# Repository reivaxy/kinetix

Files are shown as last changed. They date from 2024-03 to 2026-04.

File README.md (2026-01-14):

# KINETIX HAND

[French](https://github-com.translate.goog/reivaxy/kinetix?_x_tr_sl=en&_x_tr_tl=fr&_x_tr_hl=fr)
[Spanish](https://github-com.translate.goog/reivaxy/kinetix?_x_tr_sl=en&_x_tr_tl=es&_x_tr_hl=fr)
[German](https://github-com.translate.goog/reivaxy/kinetix?_x_tr_sl=en&_x_tr_tl=de&_x_tr_hl=fr)
[English](https://github.com/reivaxy/kinetix)

The cost is estimated less than $40, depending on where your order parts from, and the weight is less than 300g.

BOM: https://github.com/reivaxy/kinetix/blob/main/hardware/Schematics/BOM.md

Connect to your nearby KinetiX through Bluetooth here: https://reivaxy.github.io/kinetix/

> [!TIP]
> Detailed assembly instructions are available in the [wiki section](https://github.com/reivaxy/kinetix/wiki)<br/>
> 
> We suggest you read it before starting building this project to make sure you have the required tools. It is not very
> difficult, but when you don't have a soldering iron, you don't have a soldering iron 😉
> 
> **Be sure to read the "parts" chapter about the servo motors** that come in many flavors, only one of which is supported for now.

> [!TIP]
> You need not build the firmware or the android app, binaries are available in the [releases section](https://github.com/reivaxy/kinetix/releases)
> 
> **BEWARE**: for now, voice control via bluetooth is only available with the **ANDROID application**, but soon via a webpage opened in Chrome browser for all platforms where Chrome is supported.
> There is a prototype iPhone application that allows control by pressing buttons on the screen.

> [!CAUTION] 
> The work in this repository is released under licence Creative Commons 
> Attribution-NonCommercial-ShareAlike 4.0 International (CC BY-NC-SA 4.0) open-source license<br/>
> Please read this license to understand what you may and may not do with these files (software and 
> hardware):<br/> 
> https://creativecommons.org/licenses/by-nc-sa/4.0/<br/><br/>
> The 3D part of this work is based on the Kinetic Hand, created and released by Mat Bowtell:<br/>
> https://www.thingiverse.com/thing:4618922<br/><br/>
> To me, the most important part of it is "non commercial": do not use this work to sell anything, 
> in any way, no matter how derivative it is.<br/><br/>
> =============== DISCLAIMER of liability =============== <br/>
> This is not a medical device. You must not use it as a missing limb replacement without checking with
> medical professionals if this is appropriate.<br/>
> Also, this is still a work in progress and should not be used until it has reached some level of 
> completion and testing.<br/>  
> You build it and use it at your own risks.  
> 
> Contributions are welcome, please try as much as possible to respect the [contribution guidelines](./CONTRIBUTING.md), thanks!

Main features (WIP): 5 independantly controlled fingers, bluetooth connexion to control movements from a mobile phone, edit settings, wirelessly update the firmware (using also Wifi), extensibility to add sensors and more.

I've been a maker and board member of [the French e-Nable association](https://e-nable.fr/fr/) for a few years, and I've 
worked on several 3D printed devices intended for people missing part of a hand or an arm.

The most recent of these devices is the [Kinetic hand, designed by Mat Bowtell](https://www.thingiverse.com/thing:4618922), which is easy to print and assemble, with 
a smoother and more natural look than older devices such as the Phoenix Unlimbited.

These devices are muscle activated and require their user to still have a functional wrist or an elbow.
When I worked on this project, there was only one low cost motor activated 3D printed device, the [Exii Hackberry](https://www.exiii-hackberry.com/) with all the documentation needed to build it.
It's a great device, but I found it somehow uneasy to print and assemble, with many small fragile parts, it's still a bit expensive, and I thought
more recent electronic components would allow going further.

Which is why in 2023 I started to work on this project to combine both new hand design, and recent 
electronic microcontroller to drive the servomotors. I've investigated several solutions and here is the most promising one.

This is still very much a Work In Progress:
- The bluetooth connectivity is not secured, and voice control will work with anyone's voice.
- The wires tension is not adjustable
...

Like the Hackberry and unlike the Kinetic, due to tight mechanical constraints, the Kinetix can't be resized to fit smaller limbs.
I have another project (in very early stage) which might help with this, that is using only one big servo for all fingers, of course with
very different capabilities and features.

Adding a small "shield" board on top of main board, capabilities can easily be extended. This videos shows tests with a very simple pressure sensor:

https://github.com/user-attachments/assets/475526ec-1bb6-489a-a5ff-d1ec1696035d

Since May 12th 2024, it can be activated with voice control using an Android application (please enable sound on this video or it won't make much sense :) )

https://github.com/reivaxy/kinetix/assets/3592991/68d8df24-c723-40e2-a849-26ecd64f889a

And here was the early first prototype, testing speed:

https://github.com/reivaxy/kinetix/assets/3592991/b644f965-3c86-4bcd-a1fd-c3cf471b4016

Check [latest release](https://github.com/reivaxy/kinetix/releases/) for APK with voice control

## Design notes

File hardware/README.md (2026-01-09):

June 22 2024:

New version v0.4 without current monitoring but much easier to mount with a simple soldering iron (no SMDs).

This new design is modular and allows to plug an additional pcb or proto-board with specific circuitry
for instance for current monitoring or for specific sensors, etC.

Information about the board in the wiki:

https://github.com/reivaxy/kinetix/wiki/04.-Electronic-Board

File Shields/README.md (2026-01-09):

# Shields for the KinetiX main board

These are electronic boards that can be added on top of the main KinetiX board to extend its capabilities.

It takes advantage of the pins mounted on the main board to access the GPIOs of the ESP as well as the power line of the servos.

More information about the shields in the wiki:

https://github.com/reivaxy/kinetix/wiki/10.-Extension-Shields

Oled screen: https://github.com/reivaxy/kinetix/wiki/10b.-Oled-debugging-screen

Pressure sensor: https://github.com/reivaxy/kinetix/wiki/10a.-Pressure-sensor-activation

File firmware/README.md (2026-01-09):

# Software

Folder esp32 contains the actual software for the Seeed Studio XIAO ESP32S3

Beware, it won't work with the Seeed Studio XIAO ESP32C3 (C3 vs S3), some modifications would be required in the servomotor command.

You can find some information about installing the firmware in the wiki: 

https://github.com/reivaxy/kinetix/wiki/05.-Firmware

And some explanation about the code itself:

https://github.com/reivaxy/kinetix/wiki/05.-Firmware#the-code

Folder rp2040 contains preliminary tests with an early prototype on breadboard, and is no longer maintained.

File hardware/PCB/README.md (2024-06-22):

# PCB

There was a little bug on PCB v0.3, which is fixed in v0.4

If you already have or ordered version v0.3 let me know, it can be fixed with a little wire, and would only impact extension boards.

This PCB was created using the online schema and pcb editors from https://easyeda.com/editor

It only uses standard parts easy to solder with a soldering iron (SMD capacitor c1 is not mandatory)

The gerber zip file can be used to order PCBs. I ordered mine from https://jlcpcb.com, where I could get 5 pieces for under $5 shipping included.

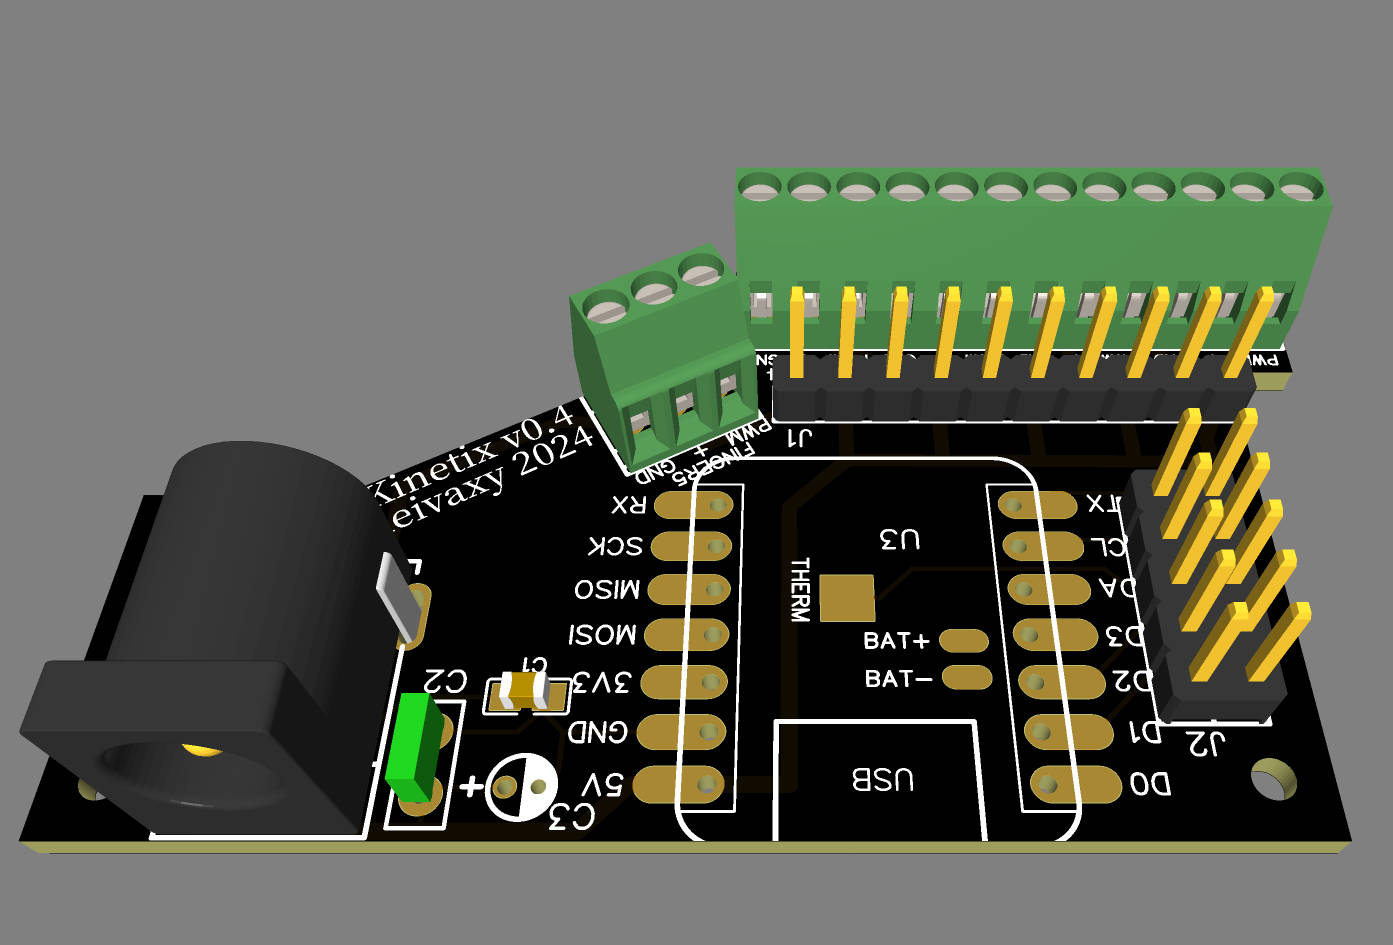
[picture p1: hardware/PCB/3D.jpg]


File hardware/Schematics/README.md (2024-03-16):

# Schematics

This schematic was created using the online schema and pcb editors from https://easyeda.com/editor

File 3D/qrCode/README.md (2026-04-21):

A small QR code stand you can use if you present a KinetiX hand at a maker fair or conference or whatever.



Should be printed in at least two colors, of course.



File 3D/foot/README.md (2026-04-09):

This is a simple foot or stand to hold your KinetiX upright.

You will need to print the "key" part twice, preferably in TPU.



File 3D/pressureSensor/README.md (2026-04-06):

# Pressure sensor case

The base is printed in PLA, the press in TPU.

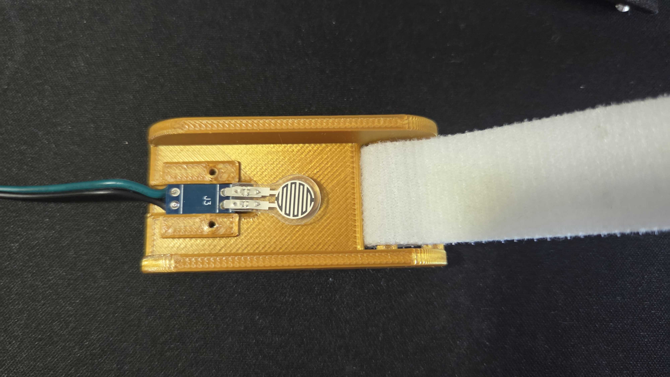
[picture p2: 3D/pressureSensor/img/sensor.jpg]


A small piece of pcb is used to hold the sensor in place, and it's then cover with a TPU piece ensuring a soft press on the sensor.

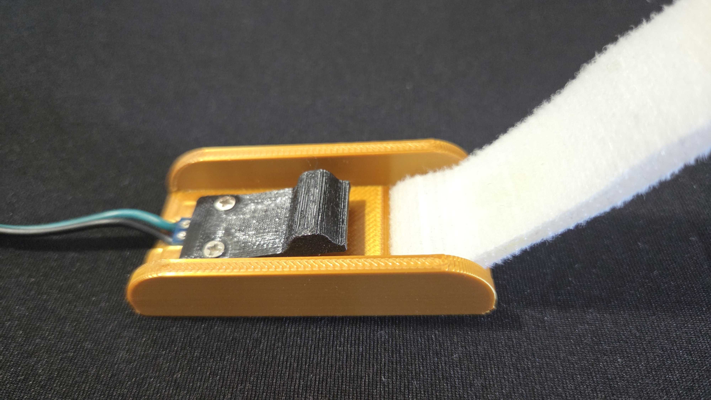
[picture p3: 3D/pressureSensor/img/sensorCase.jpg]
 

The arm band must first cover the sensor (to the left on the picture), then go around the arm, then up trough the case slot, then back around the arm and scratch to the part above the case.

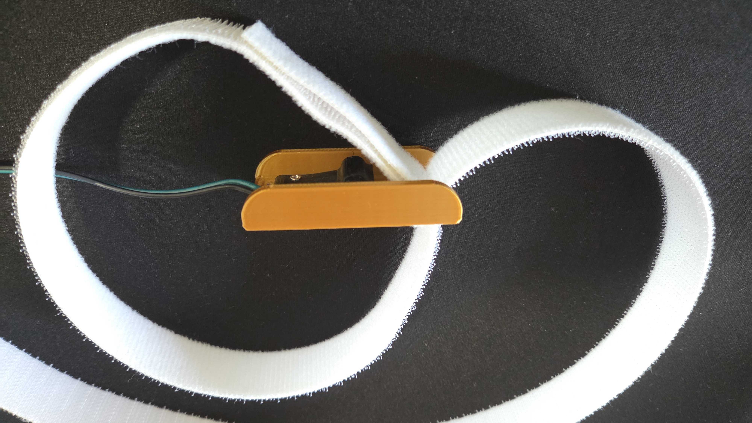
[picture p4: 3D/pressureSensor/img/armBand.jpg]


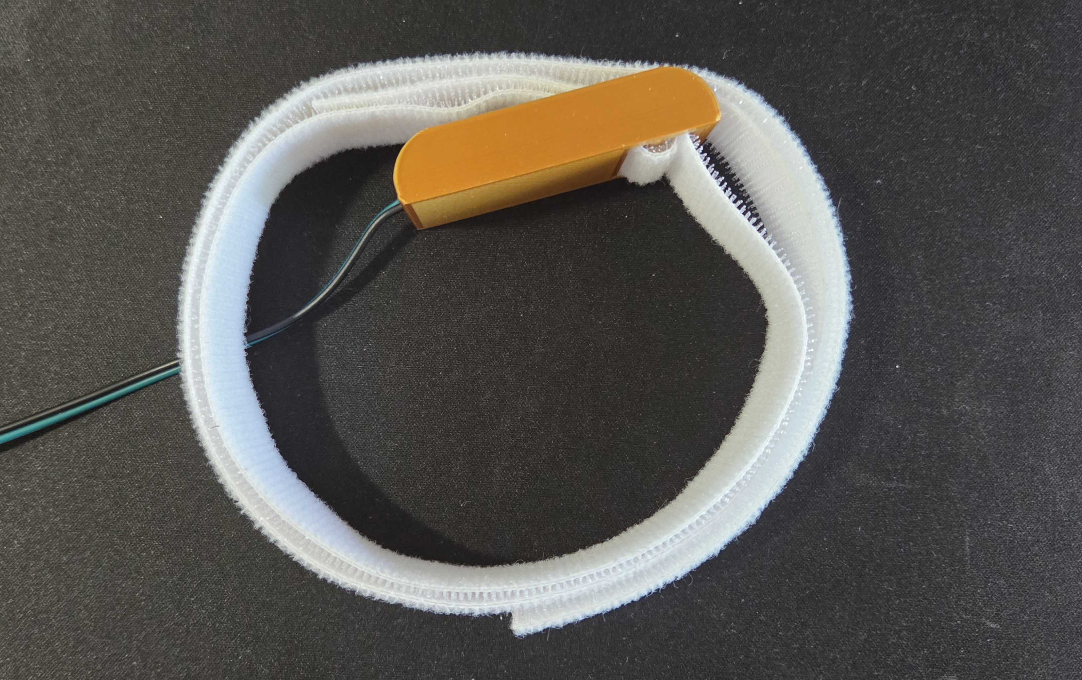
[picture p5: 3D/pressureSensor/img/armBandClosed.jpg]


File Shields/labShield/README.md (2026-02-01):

# The Lab Shield

The purpose of the lab shield is to offer an easy prototyping platform to test your ideas about sensors, monitoring, etc.
It's a simple board that can be mounted on the KinetiX main board and exposes the ESP32 GPIOs as well as the servomotors 
power supply line.

Of course most (if not all) applications will need a modified firmware.

It is equipped with many pads to solder extra components, but does nothing in itself.

Once an idea is tested and tweaked using this shield, a new specific PCB can easily be made from the same source files.

Here is the first version.



It was used to connect a [pressure sensor](https://github.com/reivaxy/kinetix/wiki/10a.-Pressure-sensor-activation), and an [OLED screen](https://github.com/reivaxy/kinetix/wiki/10b.-Oled-debugging-screen)

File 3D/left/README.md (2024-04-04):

# STL files to print a left hand

They are just a symmetry from the right hand files, which is why the engraved numbers are also reversed.

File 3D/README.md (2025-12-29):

# KINETIX HAND

This work is based on the Kinetic Hand, created and released by Mat Bowtell:
https://www.thingiverse.com/thing:4618922
                                                 
This work is released under licence Creative Commons Attribution-NonCommercial-ShareAlike 4.0 International (CC BY-NC-SA 4.0) open-source license

Please read this license to understand what you may and may not do with these files:

https://creativecommons.org/licenses/by-nc-sa/4.0/

Here are some printing instructions that can be helpful: https://github.com/reivaxy/kinetix/wiki/01.-Printing

The "common" folder contains parts that fit both right side hands and left side hands.

The "left" folder contains parts for a left side hand, and the "right" folder... well you know.

leftAndRight

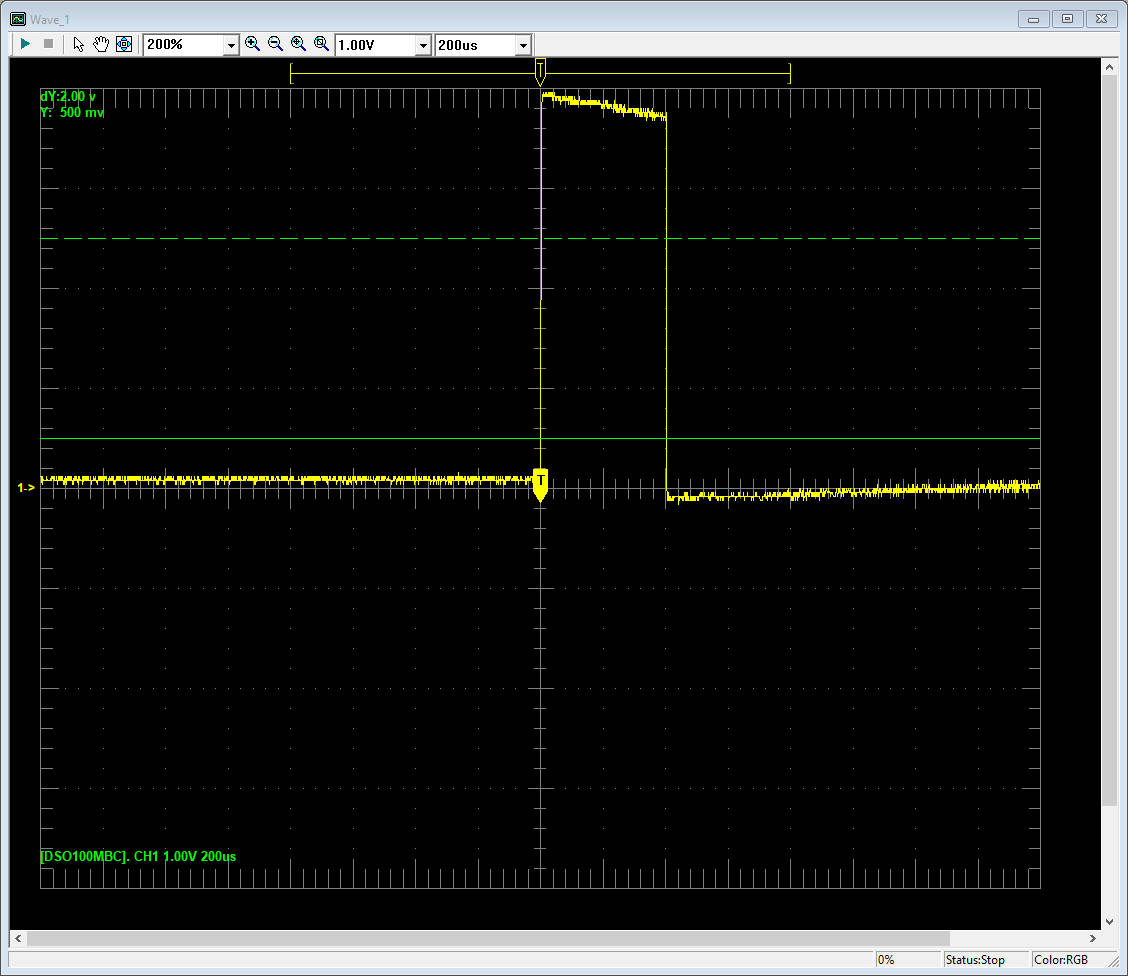
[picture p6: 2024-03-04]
firmware/rp2040/img/MG90s_min.jpg

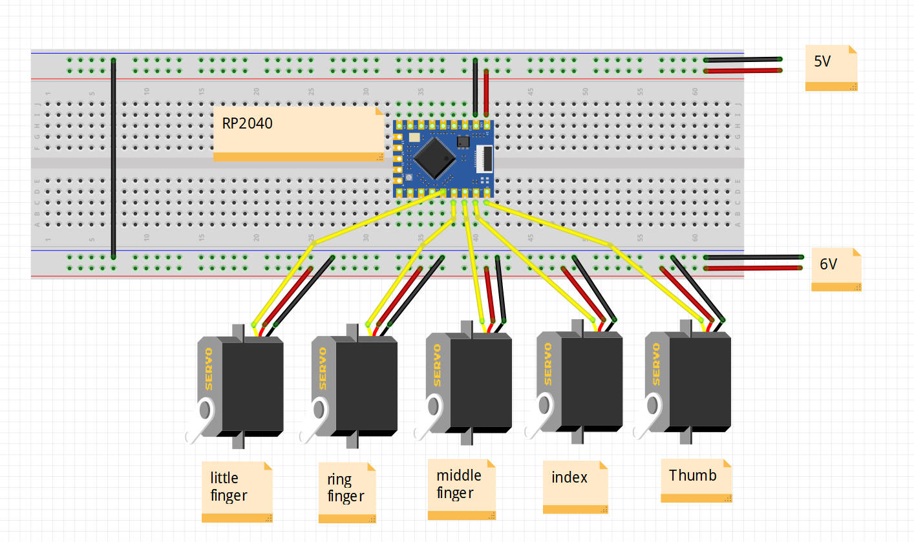
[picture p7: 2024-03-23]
firmware/rp2040/img/rp2040.jpg

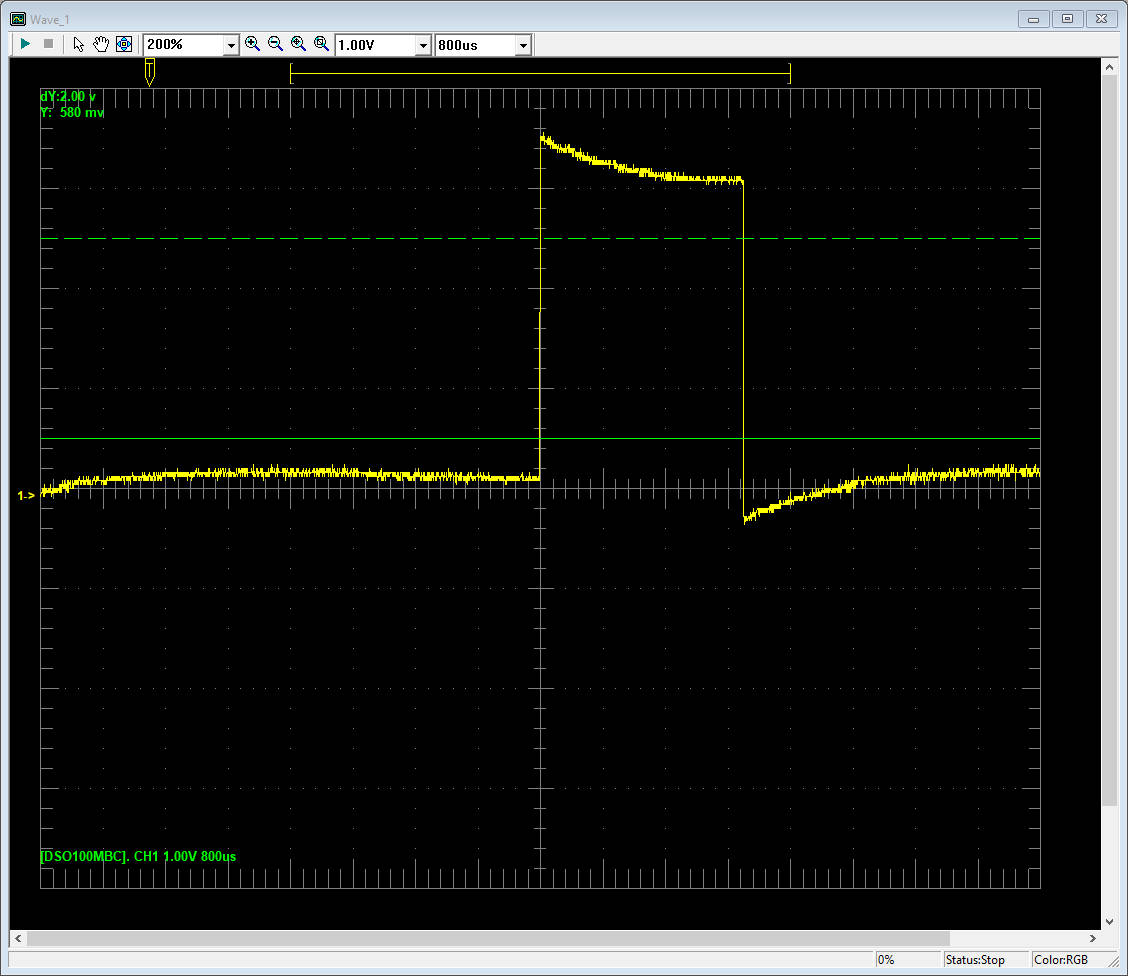
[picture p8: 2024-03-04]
firmware/rp2040/img/MG90s_max.jpg

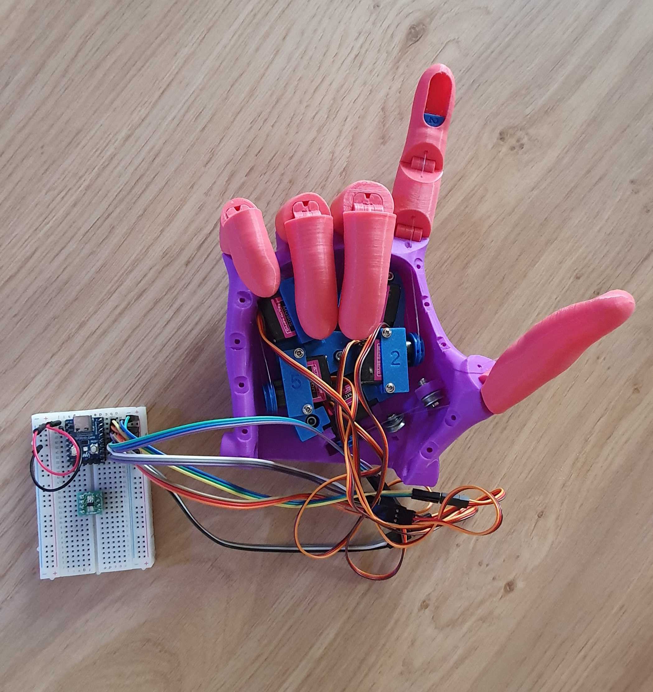
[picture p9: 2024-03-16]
firmware/rp2040/img/handRP2040.jpg

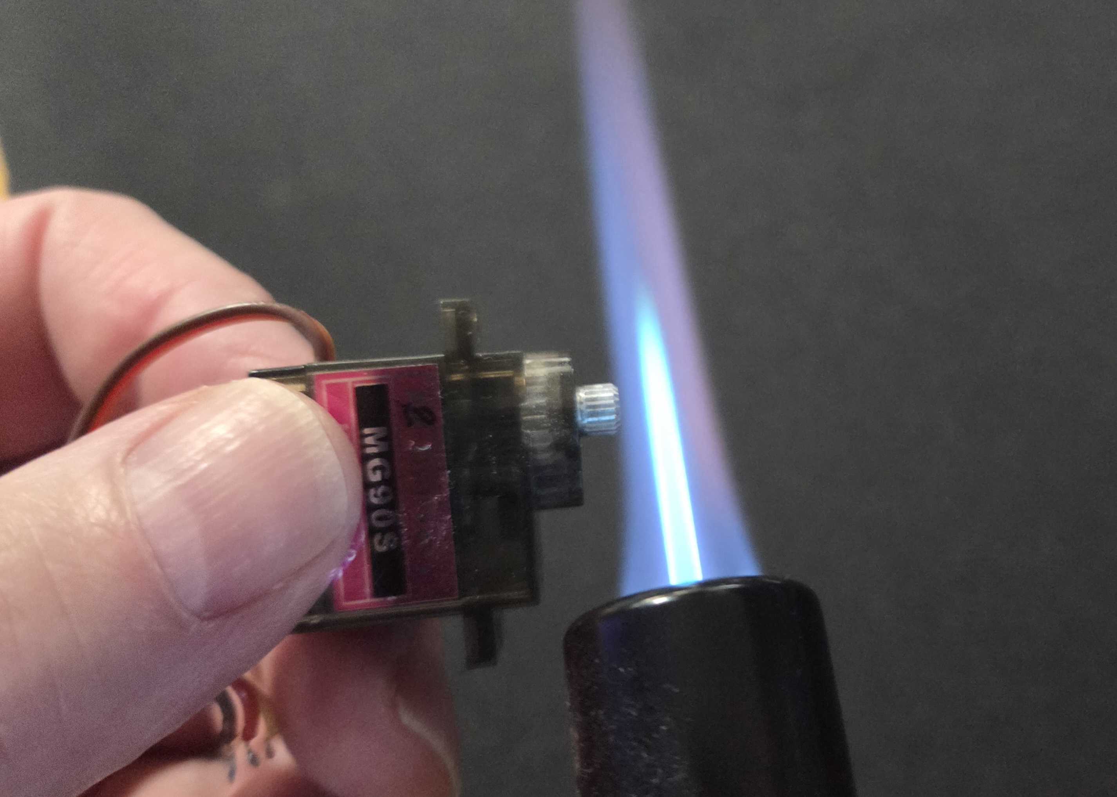
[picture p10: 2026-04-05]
3D/common/tighterPulleys/img/heating.jpg

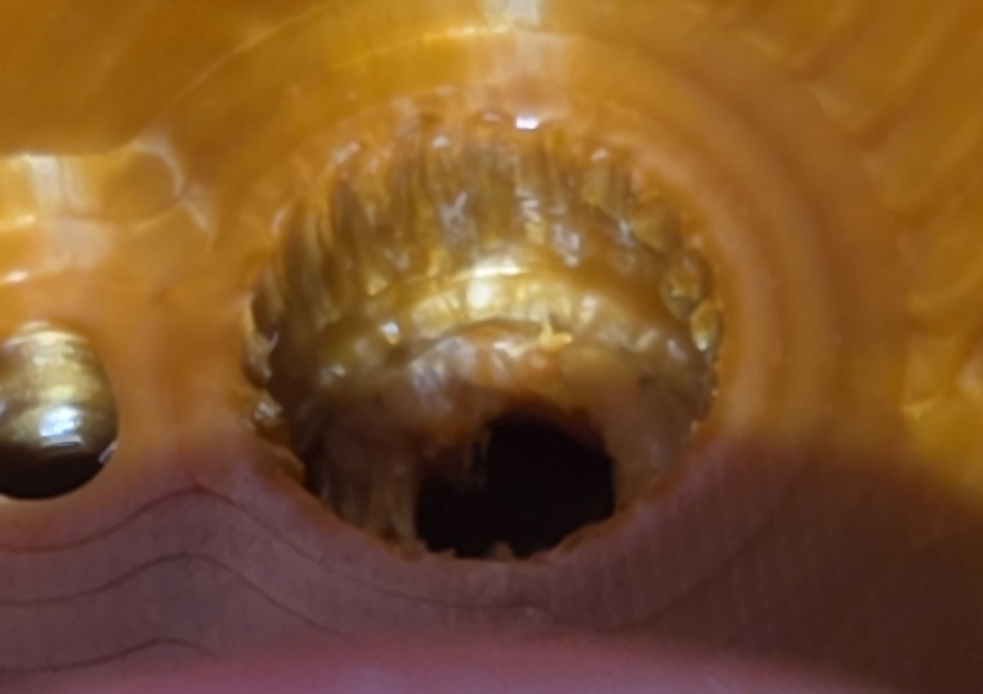
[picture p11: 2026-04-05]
3D/common/tighterPulleys/img/shaft_after.jpg

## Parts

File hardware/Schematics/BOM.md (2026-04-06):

Here is a BOM with links to find the parts. Find equivalents to the french links should not be an issue.

Please notify us when links are dead.

|Count| Item | Link |
|------|------|------|
| 1 | Esp32 | https://www.mouser.fr/ProductDetail/Seeed-Studio/113991114?qs=3Rah4i%252BhyCEHk7Z4Wa73Xg%3D%3D |
| 1 | DC power jack | https://www.ebay.com/itm/313926582472 |
| 2 | 6 pins PCB screw terminal | https://www.ebay.com/itm/185844923992 |
| 1 | 3 pins PCB screw terminal | https://www.ebay.com/itm/185844923992 |
| 1 | PCB | https://jlcpcb.com/ |
| 2x5 and 1x10  | pin terminals | https://www.ebay.com/itm/173307509367 |
| 5 | jumpers | https://www.ebay.com/itm/166501125147 |
| 1 | Capacitor 100µF 16V | https://www.ebay.com/itm/252361121827 |
| 1 | Capa 22nF | https://www.ebay.com/itm/161376440730 |
| 5 | Servomotors MG90S 180° | https://www.amazon.fr/Miuzei-engrenages-servomoteurs-Arduino-Mod%C3%A9lisme/dp/B0D7ZW6LSW |
| 2 | Pulleys V623ZZ | https://www.amazon.fr/3x12x4mm-Roulement-Syst%C3%A8me-Mouvement-Lin%C3%A9aire/dp/B07GVLFWRC |
| 4 | Screws M2*6 philips self tapping | https://www.amazon.fr/sourcing-map-Inoxydable-Phillips-Autotaraudeuse/dp/B01KXTUCM8 |
| 5 | Screws M3*12 hex | https://www.amazon.fr/Kozelo-100Pcs-T%C3%AAte-Cylindrique-Creux/dp/B0DG2HYT8T |
| 3 | Nuts M3 | https://www.amazon.fr/Hexagonal-filet%C3%A9es-boulons-Visserie-inoxydable/dp/B0DCXVB3ZT |
| 3 | washers M3x7 | https://www.amazon.fr/Rondelles-m%C3%A9tal-INOX-Rondelle-inoxydable/dp/B0FHN8XJ77 |
| 12 | Screws M3*10 philips self tapping | Only if you print the TPU cover, which is optional.

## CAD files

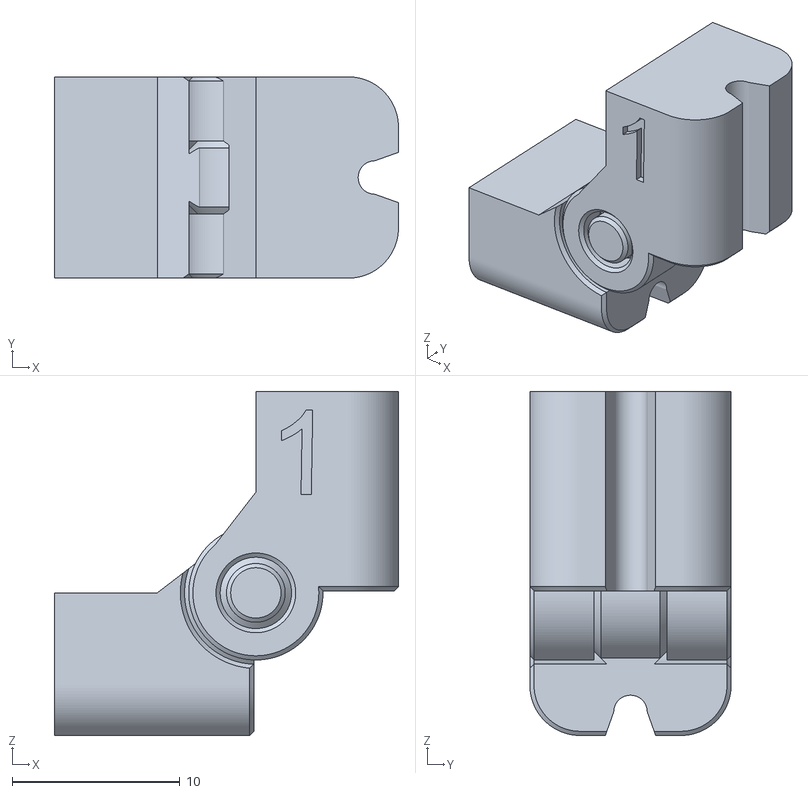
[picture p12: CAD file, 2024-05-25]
3D/common/easierKnuckles/higherTolerance/knuckle_1_0.25.stl
20.5 x 12.0 x 20.5

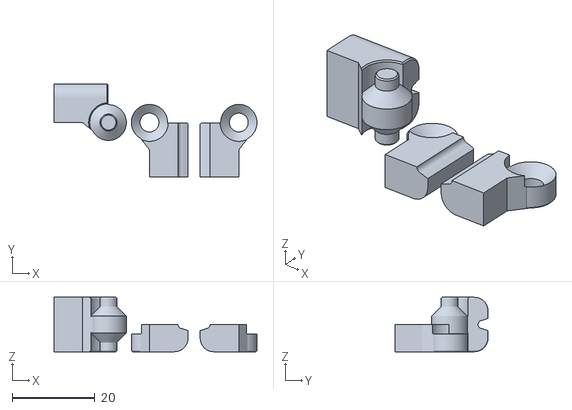
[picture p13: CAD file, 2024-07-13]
3D/common/easierKnuckles/splitKnuckles/splitKnuckle_1.1.stl
49.2 x 22.6 x 13.2

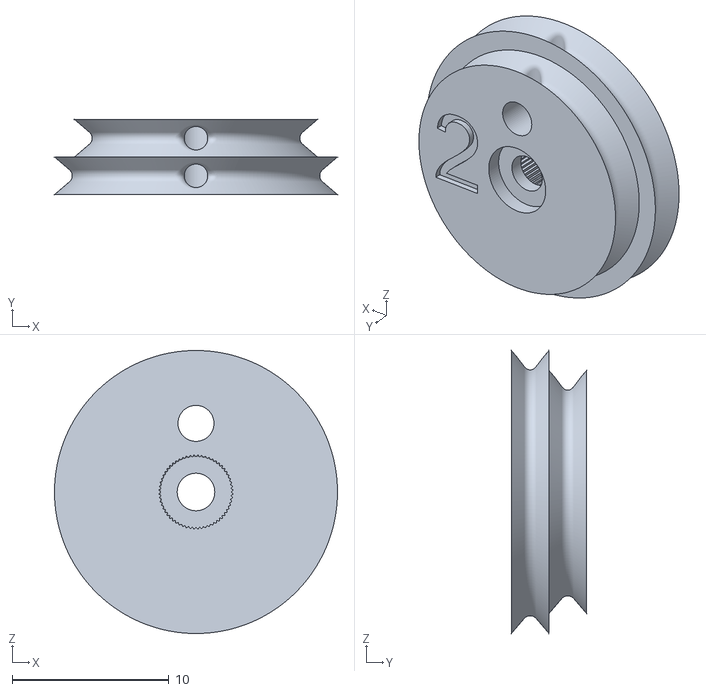
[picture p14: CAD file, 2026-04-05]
3D/common/tighterPulleys/180Pulley2Tight.stl
18.1 x 4.80 x 18.1

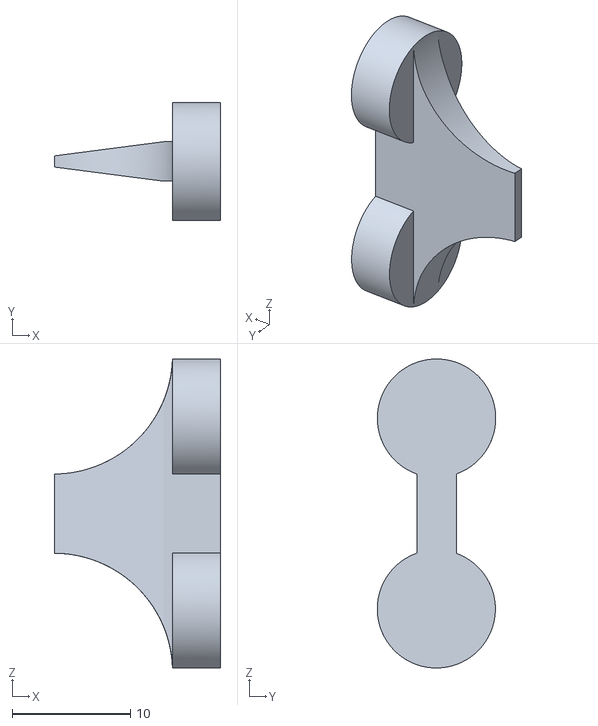
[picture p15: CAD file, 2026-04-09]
3D/foot/key.stl
14.1 x 10.0 x 26.2

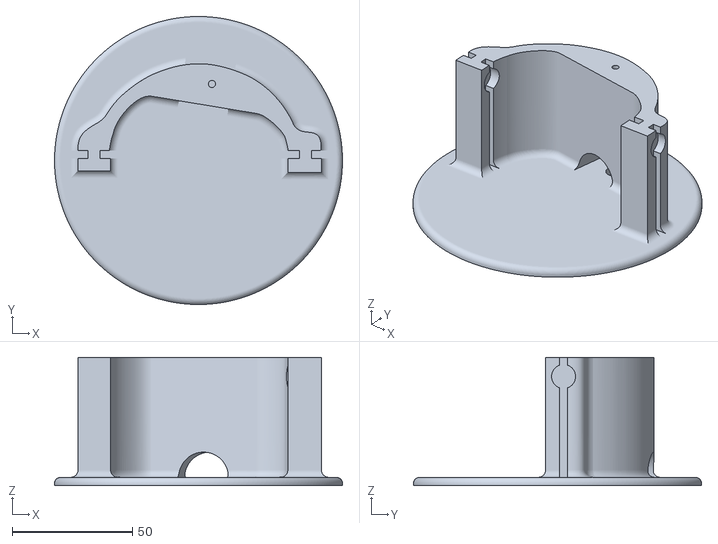
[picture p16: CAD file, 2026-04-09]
3D/foot/left/foot.stl
120.0 x 120.0 x 53.5

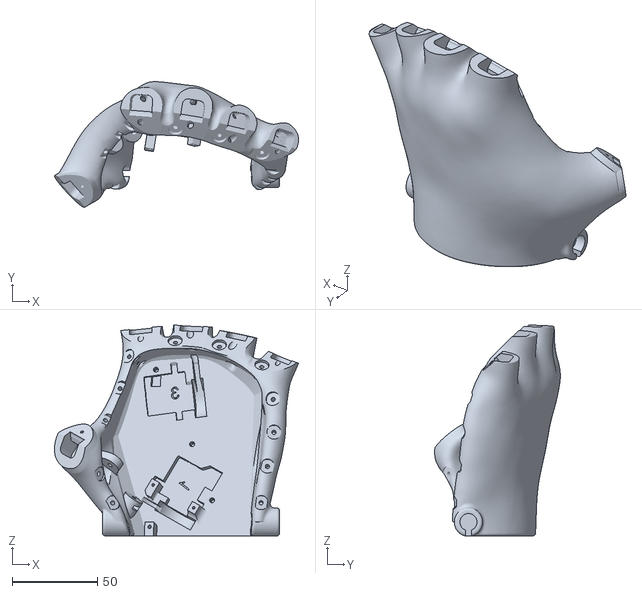
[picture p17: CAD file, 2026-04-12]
3D/left/palmL.stl
143.4 x 73.9 x 124.0

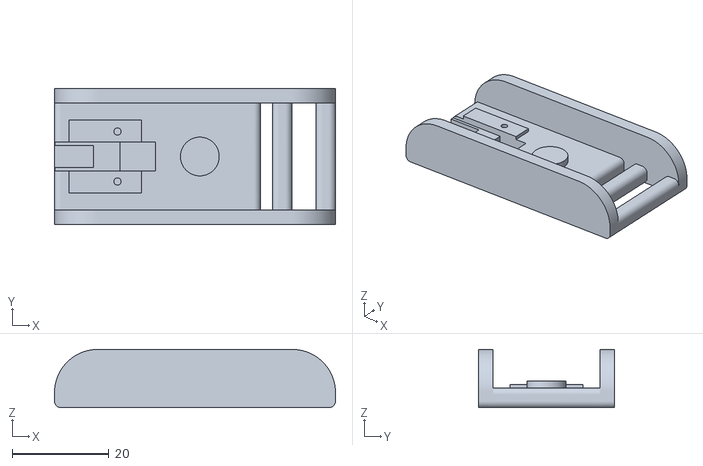
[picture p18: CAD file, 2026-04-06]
3D/pressureSensor/pressureSensorCase.stl
58.0 x 28.0 x 12.0

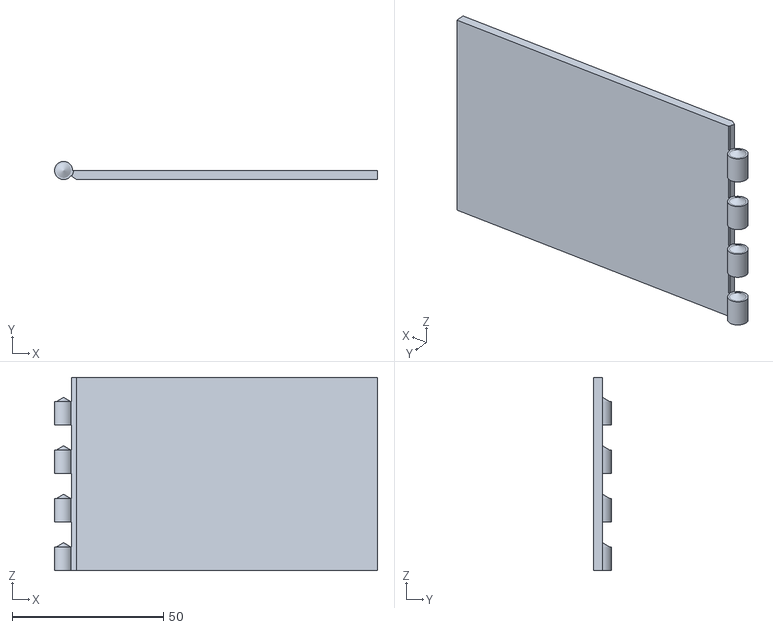
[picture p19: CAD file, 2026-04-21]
3D/qrCode/QRCode v5_QRCode v5_Body1.stl
106.7 x 6.00 x 63.8

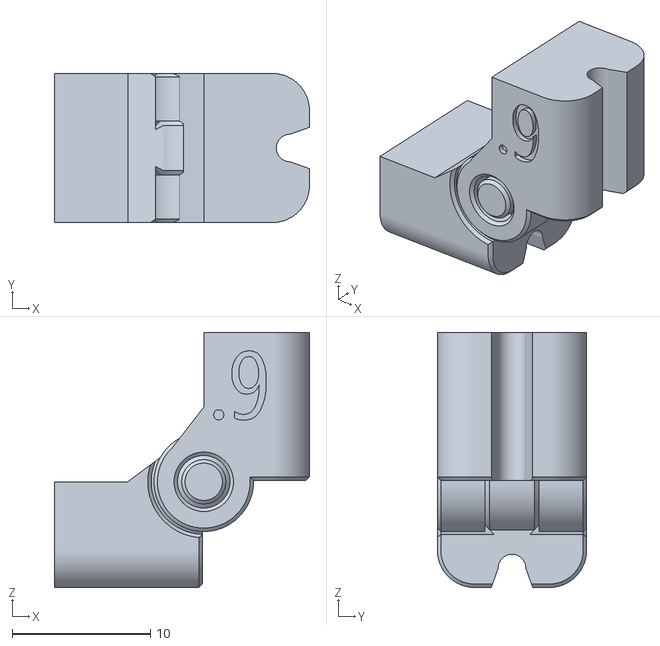
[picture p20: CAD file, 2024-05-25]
3D/common/easierKnuckles/higherTolerance/knuckle_0.9_0.2.stl
18.5 x 10.8 x 18.5

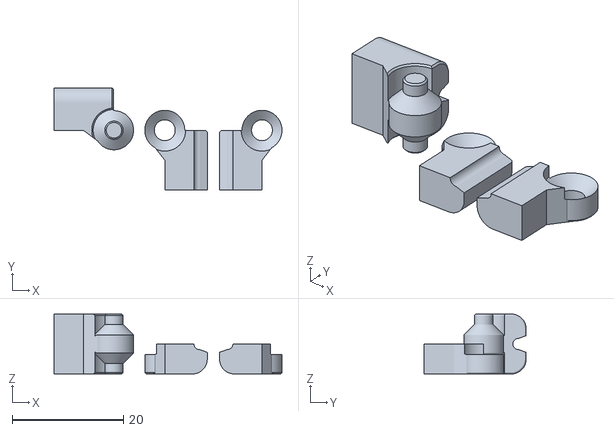
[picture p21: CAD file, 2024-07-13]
3D/common/easierKnuckles/splitKnuckles/splitKnuckle_0.9.stl
41.1 x 18.4 x 10.8

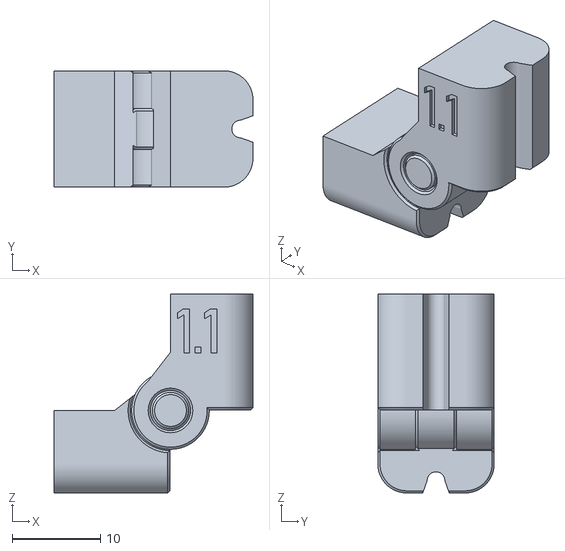
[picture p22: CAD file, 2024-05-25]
3D/common/knuckle_1.1.stl
22.5 x 13.2 x 22.6

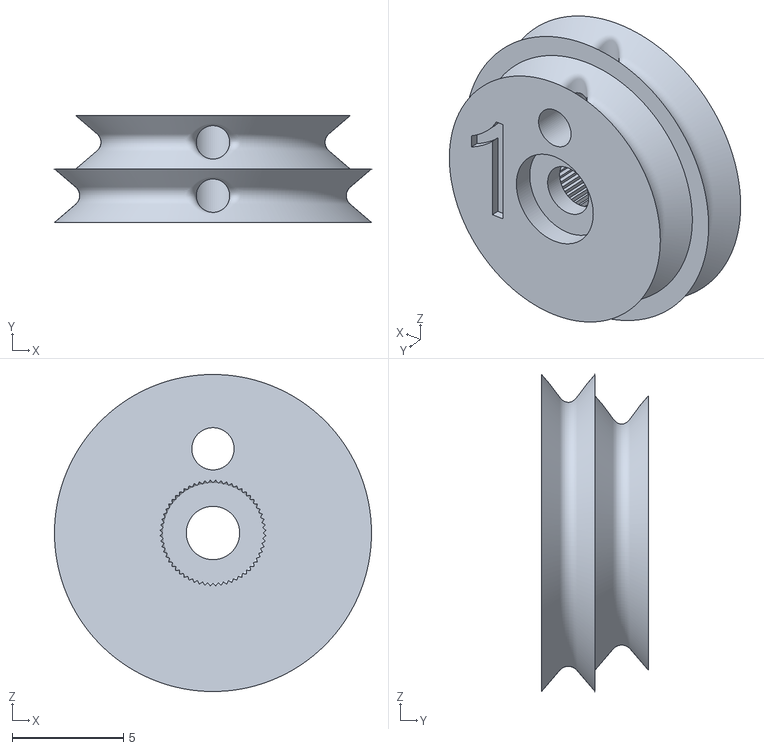
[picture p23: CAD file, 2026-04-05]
3D/common/tighterPulleys/180Pulley1Tight.stl
14.3 x 4.80 x 14.3

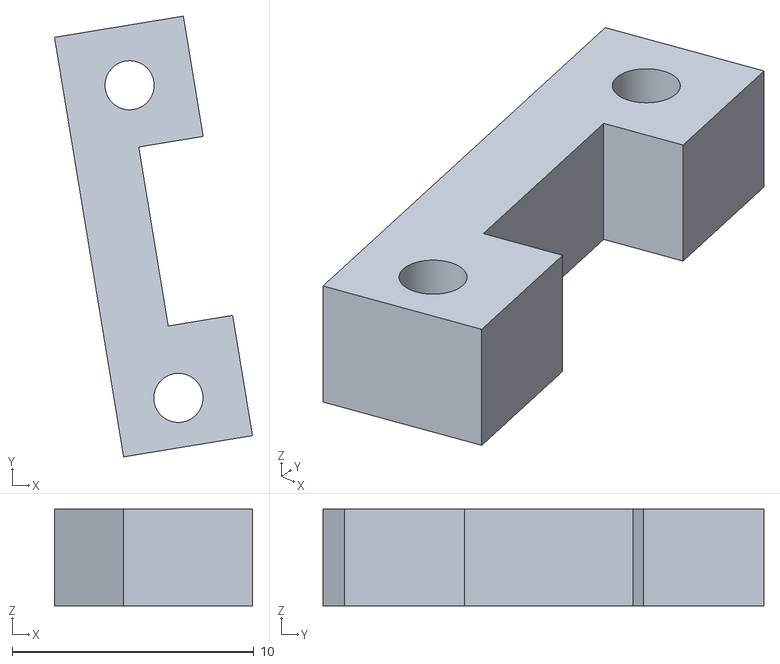
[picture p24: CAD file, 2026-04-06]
3D/left/boardSpacer1.stl
8.19 x 18.2 x 4.00

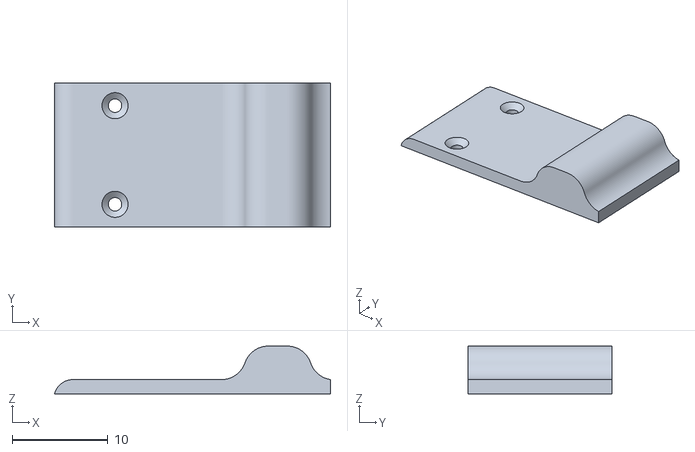
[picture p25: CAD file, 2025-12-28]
3D/pressureSensor/tpuPress.stl
28.8 x 15.0 x 5.00

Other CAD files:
3D/common/knuckle_1.stl
3D/foot/right/foot.stl
3D/right/palm.stl
3D/step/180Pulley2.step
3D/common/180Pulley1.stl
3D/common/180Pulley2.stl
3D/common/180Pulley3.stl
3D/common/180Pulley4.stl
3D/common/180Pulley5.stl
3D/common/easierKnuckles/higherTolerance/knuckle_0.9_0.25.stl
3D/common/easierKnuckles/higherTolerance/knuckle_1.1_0.2.stl
3D/common/easierKnuckles/higherTolerance/knuckle_1.1_0.25.stl
3D/common/easierKnuckles/higherTolerance/knuckle_1_0.2.stl
3D/common/easierKnuckles/splitKnuckles/splitKnuckle_1.stl
3D/common/knuckle_0.9.stl
3D/common/nutTool.stl
3D/common/tighterPulleys/180Pulley3Tight.stl
3D/common/tighterPulleys/180Pulley4Tight.stl
3D/common/tighterPulleys/180Pulley5Tight.stl
3D/left/TPUcoverL.stl
3D/left/boardSpacer2.stl
3D/left/finger 2BL.stl
3D/left/finger 3BL.stl
3D/left/finger 4BL.stl
3D/left/finger 5BL.stl
3D/left/platformL.stl
3D/left/servo2CoverL.stl
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

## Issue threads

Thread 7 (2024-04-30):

### ISSUE TITLE
Update PCB so that it can be mounted upside down on a left hand

### ISSUE THREAD

**Issue by reivaxy** [reivaxy/kinetix#7]
Right now some mounting screw holes are to close to components to rest on plastic support if the PCB is placed upside down in a left hand (printed using just a symmetry on the STL)

**Comment by reivaxy** [comment]
3 screws are fine

**Comment by Tomlabroussey2** [comment]
how do i get the motherboard for the hand? is there a tutorial on how to build the hand?

**Comment by reivaxy** [comment]
> how do i get the motherboard for the hand? is there a tutorial on how to build the hand?

Hi Tom, the wiki section has the instruction for building the hand: https://github.com/reivaxy/kinetix/wiki
As for the board, you can order it from JLCPCB as described here: https://github.com/reivaxy/kinetix/wiki/04.ElectronicBoard
You'll still need to solder the components on it.

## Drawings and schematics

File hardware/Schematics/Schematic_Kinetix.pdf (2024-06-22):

## VCC

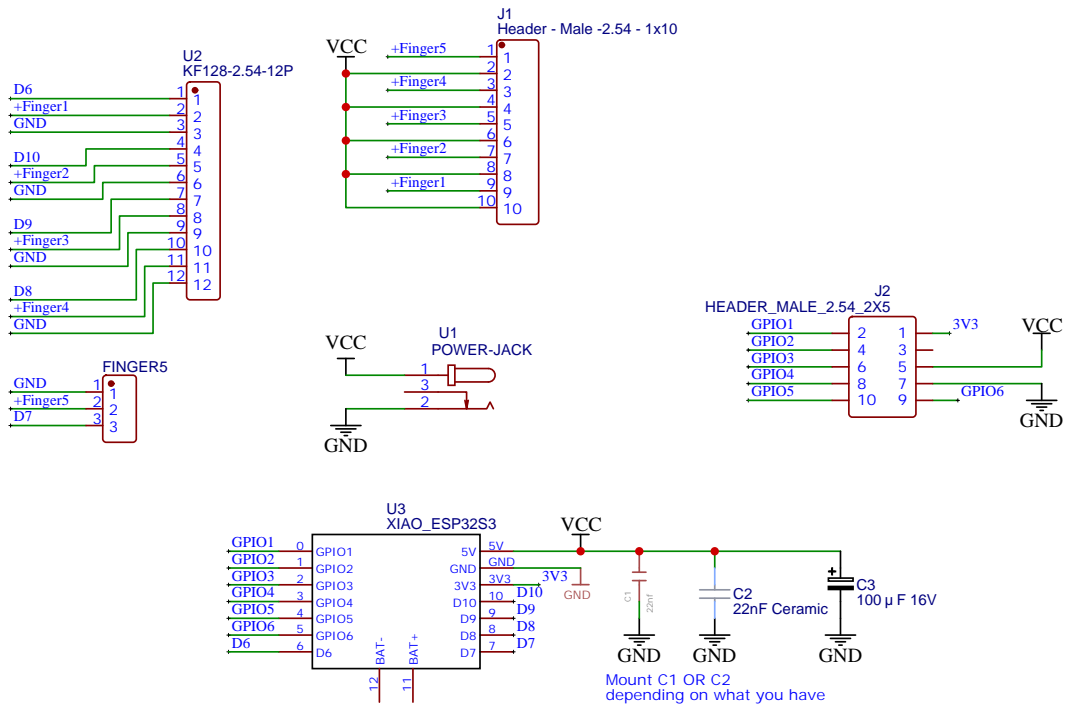
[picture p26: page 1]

GND
Mount C1 OR C2
depending on what you have

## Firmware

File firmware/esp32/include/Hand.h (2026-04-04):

#pragma once
#include <Arduino.h>
#include <driver/adc.h>

#include "Finger.h"
#include "FingerMovement.h"

#include "Settings.h"
#include "OptionalDisplay.h"

#define FINGER_COUNT 5

/*
 *   Thumb pulley expects 120°, other pulleys expect 180°
 */
#define THUMB_CTRL_PIN D6

#define FINGER1_CTRL_PIN D10

#define FINGER2_CTRL_PIN D9

#define FINGER3_CTRL_PIN D8

#define FINGER4_CTRL_PIN D7

/* Fingers 3 and 5 servos are mounted in oposite direction so their min and max are reversed compared to other fingers. */
/* Left hand and right hand are symetrical so min and max need to be reversed */
/* servos homing is supposed to be done before wiring, when servos can go full range from 0 to 180° */


#ifdef LEFT_HAND
   #define SERVO_CALIBRATION_OPEN 180
   #define SERVO_CALIBRATION_CLOSED 0

   #define THUMB_MAX_OPEN 170
   #define THUMB_MAX_CLOSED 30

   #define FINGER1_MAX_OPEN 180 
   #define FINGER1_MAX_CLOSED 10

   #define FINGER2_MAX_OPEN 20
   #define FINGER2_MAX_CLOSED 180

   #define FINGER3_MAX_OPEN 180
   #define FINGER3_MAX_CLOSED 10

   #define FINGER4_MAX_OPEN 15
   #define FINGER4_MAX_CLOSED 170
#else
   #define SERVO_CALIBRATION_OPEN 0
   #define SERVO_CALIBRATION_CLOSED 180

   #define THUMB_MAX_OPEN 30
   #define THUMB_MAX_CLOSED 180

   #define FINGER1_MAX_OPEN 10 
   #define FINGER1_MAX_CLOSED 180

   #define FINGER2_MAX_OPEN 180
   #define FINGER2_MAX_CLOSED 0

   #define FINGER3_MAX_OPEN 0
   #define FINGER3_MAX_CLOSED 180

   #define FINGER4_MAX_OPEN 180
   #define FINGER4_MAX_CLOSED 35
#endif


class Hand {
public:
   Hand(Settings *settings);

   Finger *fingers[5]; // 0 is thumb

   void close();
   void close(uint finger);
   void setCalibration(boolean);
   void updateMaxPositionsFromSettings();

   void open();
   void open(uint finger);

   bool isStill();
   bool isStill(uint finger);

   void setStep(float step);
   void setStep(int finger, float step);

   void setFinger(uint finger, FingerMovement *fingerMovement);
   void run();
   void run(uint finger);
   void stop();
   void stop(uint finger);
   void moveRelative(int to);
   Settings *settings;
};

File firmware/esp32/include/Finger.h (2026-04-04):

#pragma once

#include <Arduino.h>
#include <Servo.h>
#include "FingerMovement.h"

class Finger {
public:   
   Finger(int number, int controlPin, int maxOpen, int maxClosed, int direction);

   void move(int to);
   void computeTarget(int to);
   void refresh();
   void setStep(float step);
   void setMaxOpen(int max);
   void setMaxClosed(int max);
   void setMax(int maxOpen, int maxClosed);
   void close();
   void open();
   void run();
   void stop();
   bool isStill();
   void setMovement(FingerMovement *fingerMovement);
   void resetMovement();
   
   Servo myServo;

   int number = 0;
   int controlPin = D6;
   int maxOpen = 0; 
   int maxClosed = 180;
   time_t movementStartedAt = 0;
   uint32_t delay = 0;
   float currentPosition = maxOpen;
   int currentNormalizedPosition = 0;
   int target = maxOpen;
   int frequency = 100;
   float step = DEFAULT_STEP;
   int direction = 1;
};

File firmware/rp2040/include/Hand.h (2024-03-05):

#pragma once
#include <Arduino.h>
#include "Finger.h"
#include "FingerMovement.h"

/*
 *   6, 28 is 180°, but thumb pulley expects 120°
 */

#define THUMB_PIN 0
#define THUMB_MAX_OPEN 6.0
#define THUMB_MAX_CLOSED 18.0

#define FINGER2_PIN 1
#define FINGER2_MAX_OPEN 6.0
#define FINGER2_MAX_CLOSED 28.0

// Finger 3 (offset 2) servo is mounted on the other side => reverse commands
#define FINGER3_PIN 2
#define FINGER3_MAX_OPEN 28.0
#define FINGER3_MAX_CLOSED 9.0

#define FINGER4_PIN 3
#define FINGER4_MAX_OPEN 6.0
#define FINGER4_MAX_CLOSED 28.0

// Finger 5 (offset 4) servo is mounted on the other side => reverse commands
#define FINGER5_PIN 4
#define FINGER5_MAX_OPEN 26.0
#define FINGER5_MAX_CLOSED 10.0


class Hand {
public:
   Hand();

   Finger *fingers[5]; // 0 is thumb
   void close();
   void close(uint finger);

   void open();
   void open(uint finger);

   bool isStill();
   bool isStill(uint finger);

   void setStep(float step);
   void setStep(int finger, float step);

   void setFinger(uint finger, FingerMovement *fingerMovement);
   void run();
   void run(uint finger);
   void stop();
   void stop(uint finger);
};

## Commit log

2024-03-04 First commit, files comming from distinct proto repos
    [180Pulley1.stl, 180Pulley2.stl, 180Pulley3.stl, 180Pulley4.stl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]
2024-03-04 all fingers in sequence
2024-03-10 First schematics and PCB version 0.1
    [BOM_Kinetix.csv]
2024-03-16 added part number on fingers
    [finger 2B.stl, finger 3B.stl, finger 4B.stl, finger 5B.stl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]
2024-03-23 addng esp32s3 version
2024-03-23 First tests with current monitoring on f4
2024-03-30 First test with current monitoring on finger 5
2024-03-31 moved finger top engravings
    [finger 2B.stl, finger 3B.stl]
2024-04-04 Adding left hand files
    [finger 2BL.stl, finger 3BL.stl, finger 4B.stl, finger 4BL.stl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]
2024-04-06 added more 'left' files
    [180Pulley1.stl, 180Pulley2.stl, 180Pulley3.stl, 180Pulley4.stl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]
2024-04-25 Added left hand default configuration
    [wireBlockerFinger1L.stl, wireBlockerFinger2L.stl, wireBlockerFinger3L.stl, wireBlockerFinger4L.stl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]
2024-04-27 tighter pulley4 test
    [180Pulley4Tight.stl]
2024-04-27 Adding build configs for servos home, demo, left/right support
2024-04-28 Prototype for Android app for remote control
2024-05-06 Adding Calibration sequence
2024-05-07 more space underneath esp32 for left hand
    [platform.stl, platformL.stl]
2024-05-09 Now handling preferences to set up the Mac Address (no bluetooth device list for now)
2024-05-09 Adding About and Tools to menu Migrated the Calibratio button to Tools activity
2024-05-10 Added Scratch movement Fixed Calibration sequence Button position preference
2024-05-12 Adding TPU palm cover STLs
    [TPUcover.stl, TPUcoverL.stl]
2024-05-17 Now using onPartialResults for faster reaction Activated offline voice recognition mode New preference to de activate voice control
2024-05-19 Adding looser tolerance knuckles
    [knuckle_0.9_0.2.stl, knuckle_0.9_0.25.stl, knuckle_1.1_0.2.stl, knuckle_1.1_0.25.stl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]
2024-05-25 Easier to print knuckles
    [knuckle_0.9.stl, knuckle_1.1.stl, knuckle_1.stl]
2024-05-25 Adding easier knuckles
    [knuckle_0.9_0.2.stl, knuckle_0.9_0.25.stl, knuckle_1.1_0.2.stl, knuckle_1.1_0.25.stl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]
2024-05-26 Added bluetooth device list accessible from main menu Can now select device from list, saved in prefs.
2024-05-27 Added "Safe Filter" in preferences
2024-06-02 New thumb servo cover
    [servoThumbCover.stl, servoThumbCoverL.stl]
2024-06-03 PCB V0.3, easier and cheaper
    [BOM_Kinetix.csv]
2024-06-08 Fixed in case git is not available.
2024-06-22 Fixed v0.3 missing 3V3 net
    [BOM_Kinetix.csv]
2024-06-28 Smaller top holes on wireblockers
    [wireBlockerFinger1.stl, wireBlockerFinger1L.stl, wireBlockerFinger2.stl, wireBlockerFinger2L.stl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]
2024-07-05 Removed old misplaced left wire blockers
    [wireBlockerFinger1L.stl, wireBlockerFinger2L.stl, wireBlockerFinger3L.stl, wireBlockerFinger4L.stl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]
2024-07-08 increased height of nut canal in palm
2024-07-13 Adding split knuckle design suggested by @FALLOURD
    [knuckle_0.9_0.2.stl, knuckle_0.9_0.25.stl, knuckle_1.1_0.2.stl, knuckle_1.1_0.25.stl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]
2025-04-19 Adding step files
    [180Pulley1.step, 180Pulley2.step, 180Pulley3.step, 180Pulley4.step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]
2025-10-06 Update README.md
    Adding photo and video explaining assembling.
2025-11-30 board spacers for left hand
    [boardSpacer1.stl, boardSpacer2.stl]
2025-12-10 adding pcb source file for easyeda editor
2025-12-10 Base source file for EasyEda PCB editor for shields
2025-12-12 First implementation with analog sensor
2025-12-23 Now saving the values in the ESP32
2025-12-28 Adding pressure sensor 3D printed casing
    [base.stl, tpu.stl]
2025-12-28 Add README for pressure sensor case
    Added details about the pressure sensor case including materials and assembly notes.
2025-12-28 Update static.yml to include path filter
    Add path filter for ChromeBrowser on push events
2025-12-29 Adding PCB Json file to ease modifications
2025-12-29 Add printing instructions to README
    Added printing instructions link to README.
2025-12-29 System info now lists options (sensor, oled screen...) Sensor is really optional now without side effects Smoothing OTA progress in webapp
2025-12-29 Revise README with updated prototype videos
    Updated video links and descriptions for project status.
2025-12-30 remove incomplete BOM
    [BOM_Kinetix.csv]
2026-01-04 Adding the 'calibration' command to webpage app
2026-01-05 Add BOM link to README
    Added a link to the Bill of Materials (BOM) for the project.
2026-01-08 issue35: removed duplicated "Hand;;Run" calls. Fingers now handle their start delay themselves, much cleaner. Added a "demo" infinite sequence invoked with "demo"
2026-01-09 Update README with shield board details and video links
    Clarified the description of the shield board and updated video links for voice control activation and prototype testing.
2026-01-09 Update README with additional shield information
    Added links to wiki pages for Oled screen and Pressure sensor.
2026-02-01 Revise README for Lab Shield and add sensor references
    Removed caution note and updated image description.
2026-04-04 Settings now handle a document to store finger max positions
2026-04-04 Exposing finger max positions live tweaking
2026-04-05 Refine servomotor entry in BOM
    Updated servomotor entry with specific model and link.
2026-04-05 Tighter pulleys option
    [180Pulley1Tight.stl, 180Pulley2Tight.stl, 180Pulley3Tight.stl, 180Pulley4Tight.stl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]
2026-04-05 Added ox and cx commands to open/close each finger individually. Improved "demo", "scratch" and "come here" sequences
2026-04-06 Added reset finger max positions to factory default
2026-04-06 Thicker board spacers for left hand Much better case for pressure sensor
    [boardSpacer1.stl, boardSpacer2.stl, pressureSensorCase.stl, tpuPress.stl]
2026-04-06 removing old design
    [base.stl, tpu.stl]
2026-04-06 Better positioned spacers
    [boardSpacer1.stl, boardSpacer2.stl]
2026-04-06 Add note for optional Screws M3*10 in BOM
    Added a conditional note for Screws M3*10 regarding the TPU cover.
2026-04-12 adding missing holes to fix servo covers, and one missing PCB support
    [palm.stl, palmL.stl]
2026-04-19 Pwd now has its own setting and dialog Device name can be customized
2026-04-21 Android App now handles optional password authentication, set and reset, as well as device name edition. Added nice small QR code display for exhibitions
    [QRCode v5_QRCode v5_Body1.stl, QRCode v5_QRCode v5_Body5.stl, QRCode v5_QRCode v5_Body53.stl, QRCode v5_QRCode v5_Body54.stl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]
